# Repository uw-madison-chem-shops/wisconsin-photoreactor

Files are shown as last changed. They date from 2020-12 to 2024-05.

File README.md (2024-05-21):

# Wisconsin Photoreactor Platform (WPP)

An open source photoreactor platform. 3D printed enclosure, commercially available components, and a little bit of custom circuitry.

WPP photo

The WPP has been published in Organic Letters.
Please read our article to learn more about the motivation behind the WPP and to see examples of photochemistry being driven using this reactor.

>[Versatile Open-Source Photoreactor Architecture for Photocatalysis Across the Visible Spectrum](https://doi.org/10.1021/acs.orglett.1c01910); Philip P. Lampkin, Blaise J. Thompson, and Samuel H. Gellman; Org. Lett. 2021, 23, 13, 5277–5281

## Repository

This is an open source hardware project licensed under the CERN Open Hardware License Version 2 - Permissive.
Please see the LICENSE file for the complete license.

This repository is being mirrored to several version control systems in an attempt to ensure maximum availability.

| name             | url                                                                             |
| ---------------- | ------------------------------------------------------------------------------- |
| blaise           | https://git.blaise.zone/uw-madison-chem-shops/wisconsin-photoreactor.git/about/ | 
| Codeburg         | https://codeberg.org/uw-madison-chem-shops/wisconsin-photoreactor               |
| GitHub (primary) | https://github.com/uw-madison-chem-shops/wisconsin-photoreactor                 |
| GitLab           | https://gitlab.com/uw-madison-chem-shops/wisconsin-photoreactor                 |

## Safety

The Wisconsin Photoreactor Platform is for use by trained chemists.

WPP apparatuses utilize high-intensity light emitting diodes (LED) that can cause eye damage if proper safety precautions are not observed. 
A light-blocking shield should be utilized whenever operating a WPP apparatus.
Care must be taken to ensure the light-blocking shield employed adequately blocks light emitted by a WPP photon source from directly reaching a user.
Use of light-filtering safety glasses alongside a light-blocking shield can provide additional protection.

## Fabrication and Operation Instructions

This repository contains detailed instructions for fabrication, operation and documentation of WPP devices.
Please see [wpp-fabrication-operation.pdf](./fabrication-and-operation-instructions/wpp-fabrication-operation.pdf)

A video guide covering part sourcing, 3D-printing, electronics manufacturing, assembly and use of Wisconsin photoreactors is available on [youtube](http://www.youtube.com/watch?v=fkLr17i4FgE)

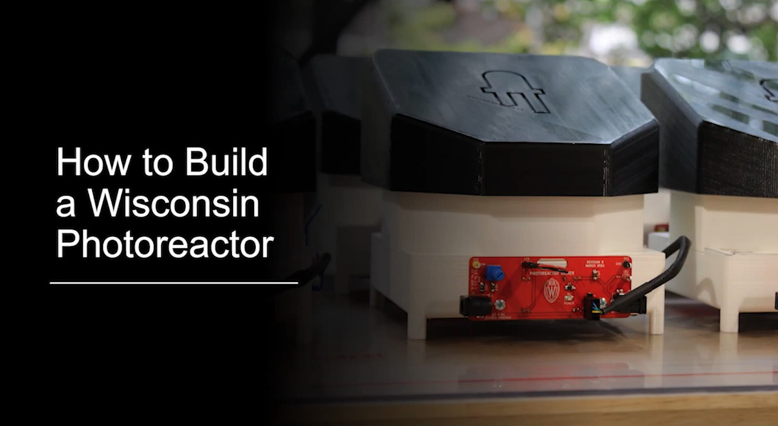
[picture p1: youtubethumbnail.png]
Wisconsin Photoreactor Platform Fabrication Video Guide (http://www.youtube.com/watch?v=fkLr17i4FgE)


## Enclosure

The WPP is designed around a mechanically robust and simple 3D printed enclosure.

Every WPP device has the same base, see directory `photoreactor-base`.
WPP reaction modules are meant to be switched based on the reaction vessel used.
See directory `photoreactor-reaction-modules` for our growing collection of reaction modules for common vessel types.
For safe WPP device operation, a light blocking shield is recommended. 
See directory `photoreactor-light-shield`, for a 3D-printable light-blocking cover for WPP devices.

## Electronics

The WPP incorporates small custom circuit boards providing control over reaction conditions.
Please see the fabrication instructions for more detailed information.

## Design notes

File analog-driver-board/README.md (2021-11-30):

# Analog Driver Board

A simple photoreactor driver board providing control over light intensity. This control is achieved through adjustment of the board-mounted potentiometer. No software is required, and multiple WPP reactors fitted with this board can be connected in series to a single power source. However, fan speed isn’t adjustable and is maintained at maximum.

Relative light intensity can be determined using the analog driver board test points and a multimeter. See operation instructions for more information.

The analog driver board is the recommended driver solution for a typical user.

## PCB

This PCB was designed using KiCAD version 5.
Refer to `driver.pdf` for schematic.
PCB images generated with [tracespace](https://github.com/tracespace/tracespace) follow.




## Bill of Materials

| reference      | value         | manufacturer | part number       | price | vendors |
| :------------- | :------------ | :----------- | :---------------- | :---- | :------ |
| C2             | 10u           | Yageo        | CC1206KKX7R8BB106 | $0.25 | [DigiKey](https://www.digikey.com/en/products/detail/yageo/CC1206KKX7R8BB106/5195365?s=N4IgTCBcDaIMJwIxgAwDYDSGAaB2ASgBwBCxi6IAugL5A) [Mouser](https://www.mouser.com/ProductDetail/Yageo/CC1206KKX7R8BB106/?qs=%2Fha2pyFadujG%252BB25mNGWlTAfaj3wXYmzjlPMfFLRNq4azOfH13S4tw%3D%3D) |
| D1             | (red)         | Lite-On      | LTST-C230KRKT     | $0.25 | [DigiKey](https://www.digikey.com/en/products/detail/lite-on-inc/LTST-C230KRKT/386857?s=N4IgTCBcDaIDIBUDKCC0BhMBmADAaQCU8EQBdAXyA) [Mouser](https://www.mouser.com/ProductDetail/Lite-On/LTST-C230KRKT/?qs=%2Fha2pyFadujtt9TjjkxDnLsTSvKz5QHldTfy80PY7mPtEP7ka44l7w%3D%3D) |
| J3, J4         | Barrel Jack   | CUI          | PJ-002A           | $1.50 | [DigiKey](https://www.digikey.com/en/products/detail/cui-devices/PJ-002A/96962) [Mouser](https://www.mouser.com/ProductDetail/CUI-Devices/PJ-002A/?qs=WyjlAZoYn51CKfAix9Mngw%3D%3D) |
| J5             | fan connector | Sullins      | PREC040SAAN-RC    | $0.50 | [DigiKey](https://www.digikey.com/en/products/detail/sullins-connector-solutions/PREC040SAAN-RC/2774814) |
| J7             | LED connector | Molex        | 0901471102        | $0.75 | [DigiKey](https://www.digikey.com/en/products/detail/molex/0901471102/3303846) |
| R1             | 6.8k          | Yageo        | RC1206FR-076K8L   | $0.10 | [DigiKey](https://www.digikey.com/en/products/detail/yageo/RC1206FR-076K8L/729028) |
| R2             | 100           | Yageo        | RC1206FR-07100RL  | $0.10 | [DigiKey](https://www.digikey.com/en/products/detail/yageo/RC1206FR-07100RL/728491?s=N4IgTCBcDaIAQCUDCBGMAGAbAMQQWnQHYV10EAZEAXQF8g) |
| R5             | 1k            | Yageo        | RC1206FR-071KL    | $0.10 | [DigiKey](https://www.digikey.com/en/products/detail/yageo/RC1206FR-071KL/728387?s=N4IgTCBcDaIEoGECMYAMA2AYnAtKg7EgNIAyIAugL5A) |
| RV1            | 2.2k          | Bourns       | 3362P-1-202TLF    | $3.00 | [DigiKey](https://www.digikey.com/en/products/detail/bourns-inc/3362P-1-202TLF/1232538?s=N4IgTCBcDaIMxwGxgAoFoCMawAYwBUAZAMRAF0BfIA) [Newark](https://www.newark.com/bourns/3362p-1-202tlf/trimmer-potentiometer-2kohm-10/dp/33M2835) |
| TP1            | (yellow)      | Keystone     | 5014              | $0.50 | [DigiKey](https://www.digikey.com/en/products/detail/keystone-electronics/5014/255336) |
| TP2            | (red)         | Keystone     | 5010              | $0.50 | [DigiKey](https://www.digikey.com/en/products/detail/keystone-electronics/5010/255332) |
| TP3            | (black)       | Keystone     | 5011              | $0.50 | [DigiKey](https://www.digikey.com/en/products/detail/keystone-electronics/5011/255333) |        |
| U2             | LED driver    | Mean Well    | LDD-1000L (pin)  | $6.00 | [DigiKey](https://www.digikey.com/en/products/detail/mean-well-usa-inc/LDD-1000L/7704722) [Allied](https://www.alliedelec.com/product/mean-well/ldd-1000l/70345765/) [Mouser](https://www.mouser.com/ProductDetail/MEAN-WELL/LDD-1000L?qs=JK6Bpmia%2FmvDNI%252Ba1vDDrA%3D%3D) [Newark](https://www.newark.com/mean-well/ldd-1000l/dc-dc-converter-analog-pwm-30w/dp/14AJ2201) [LEDSupply](https://www.ledsupply.com/led-drivers/mean-well-ldd-l-series-cc-step-down-mode)|

All prices are extended estimates in USD.
In general, these are overestimates, so this should be an upper-estimate on cost.
Many of these components can be substituted, so take the above as suggestions.
Boards themselves can be printed for approximately $5 each.

## Changelog

### Unprinted

### Revision C

#### Changed
- Removed wisconsin crest logo

#### Revision B

#### Fixed
- Fixedsign of LED terminals on silkscreen
- Voltage divider adjusted: R1 to 6.8k R2 to 100 ohm
- Adjusted voltage divider silkscreen

### Revision A

#### Added
- Initial design

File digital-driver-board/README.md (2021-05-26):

# digital-driver

A photoreactor driver board designed to be controlled digitally over I2C. For fabrication instructions, please see the fabrication and operation guide.

The digital driver is recommended for users who are experienced with electronics and interested in automating WPP devices.

## PCB

This PCB was designed using KiCAD version 5.
Refer to `driver.pdf` for schematic.
PCB images generated with [tracespace](https://github.com/tracespace/tracespace) follow.




Bill of Materials

| reference      | value         | manufacturer | part number          | price | vendors |
| :------------- | :------------ | :----------- | :------------------- | :---- | :------ |
|                | dip socket    | Mill-Max     | 110-93-308-61-001000 | $1.00 | [DigiKey](https://www.digikey.com/en/products/detail/mill-max-manufacturing-corp/110-93-308-61-001000/7734612) |
| C2             | 10u           | Yageo        | CC1206KKX7R8BB106    | $0.25 | [DigiKey](https://www.digikey.com/en/products/detail/yageo/CC1206KKX7R8BB106/5195365?s=N4IgTCBcDaIMJwIxgAwDYDSGAaB2ASgBwBCxi6IAugL5A) [Mouser](https://www.mouser.com/ProductDetail/Yageo/CC1206KKX7R8BB106/?qs=%2Fha2pyFadujG%252BB25mNGWlTAfaj3wXYmzjlPMfFLRNq4azOfH13S4tw%3D%3D) |
| C3             | 22u           | Yageo        | CC1206MKX7R7BB226    | $0.75 | [DigiKey](https://www.digikey.com/en/products/detail/yageo/cc1206mkx7r7bb226/7071713) |
| D1             | (red)         | Lite-On      | LTST-C230KRKT        | $0.25 | [DigiKey](https://www.digikey.com/en/products/detail/lite-on-inc/LTST-C230KRKT/386857?s=N4IgTCBcDaIDIBUDKCC0BhMBmADAaQCU8EQBdAXyA) [Mouser](https://www.mouser.com/ProductDetail/Lite-On/LTST-C230KRKT/?qs=%2Fha2pyFadujtt9TjjkxDnLsTSvKz5QHldTfy80PY7mPtEP7ka44l7w%3D%3D) |
| D2             | (blue)        | Lite-On      | LTST-C150TBKT        | $0.50 | [DigiKey](https://www.digikey.com/en/products/detail/lite-on-inc/LTST-C150TBKT/388526?s=N4IgTCBcDaIDIBUDKCC0BhAjAVgAwICEBpBEAXQF8g) |
| J1, J2         | i2c connector | JST          | S4B-PH-K-S(LF)(SN)   | $0.50 | [DigiKey](https://www.digikey.com/en/products/detail/jst-sales-america-inc/S4B-PH-K-S-LF-SN/926628) [Newark](https://www.newark.com/jst-japan-solderless-terminals/s4b-ph-k-s-lf-sn/connector-header-2mm-4-position/dp/38K8074) |
| J3, J4         | power input   | CUI          | PJ-002A              | $1.50 | [DigiKey](https://www.digikey.com/en/products/detail/cui-devices/PJ-002A/96962) [Mouser](https://www.mouser.com/ProductDetail/CUI-Devices/PJ-002A/?qs=WyjlAZoYn51CKfAix9Mngw%3D%3D) |
| J5             | fan connector | Sullins      | PREC040SAAN-RC       | $0.50 | [DigiKey](https://www.digikey.com/en/products/detail/sullins-connector-solutions/PREC040SAAN-RC/2774814) |
| J7             | LED connector | Molex        | 0901471102           | $0.75 | [DigiKey](https://www.digikey.com/en/products/detail/molex/0901471102/3303846) |
| PS1            | regulator     | CUI          | VXO7805-500-M-TR     | $3.00 | [DigiKey](https://www.digikey.com/en/products/detail/cui-inc/VXO7805-500-M-TR/11569188) [Newark](https://www.newark.com/cui/vxo7805-500-m-tr/non-isolated-dc-switching-regulator/dp/13AJ1536) |
| R1, R4, R6, R7 | 4.7k          | Yageo        | RC1206DR-074K7L      | $0.10 | [DigiKey](https://www.digikey.com/en/products/detail/yageo/rc1206dr-074k7l/5919134) |
| R2, R5         | 470           | Yageo        | RC1206FR-07470RL     | $0.10 | [DigiKey](https://www.digikey.com/en/products/detail/yageo/RC1206FR-07470RL/728934) |
| R3             | 10k           | Yageo        | RC1206FR-0710KL      | $0.10 | [DigiKey](https://www.digikey.com/en/products/detail/yageo/RC1206FR-0710KL/728483)  |
| U1             | microcontrol. | Microchip    | ATTINY85-20PU        | $1.50 | [DigiKey](https://www.digikey.com/en/products/detail/microchip-technology/attiny85-20pu/735469) [Newark](https://www.newark.com/microchip/attiny85-20pu/microcontroller-mcu-8-bit-attiny/dp/68T3808) |
| U2             | LED driver    | Mean Well    | LDD-1000L            | $6.00 | [DigiKey](https://www.digikey.com/en/products/detail/mean-well-usa-inc/LDD-1000L/7704722) [Allied](https://www.alliedelec.com/product/mean-well/ldd-1000l/70345765/) [Mouser](https://www.mouser.com/ProductDetail/MEAN-WELL/LDD-1000L?qs=JK6Bpmia%2FmvDNI%252Ba1vDDrA%3D%3D) [Newark](https://www.newark.com/mean-well/ldd-1000l/dc-dc-converter-analog-pwm-30w/dp/14AJ2201) [LEDSupply](https://www.ledsupply.com/led-drivers/mean-well-ldd-l-series-cc-step-down-mode)|

## I2C Interface

`<byte FAN SPEED>` `<byte LED INTENSITY>`

## Firmware

Find in "firmware" folder.

Use Arduino IDE.

We programmed the ATtiny85 using the sparkfun Tiny AVR Programmer: [PGM-11801](https://www.sparkfun.com/products/11801).

## Changelog

### Unprinted

#### Changed
- removed wisconsin crest logo

### Revision B

#### Fixed
- silk screen polarity markings for LED
- backwards I2C connectors

### Revision A

#### Added
- initial design

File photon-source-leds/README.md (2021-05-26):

# Photon Source LEDS

The WPP photon source consists of 3 high-power, single-color LEDs mounted onto an industry-standard 20 mm LED star package. 

WPP-compatible LED stars emitting narrow wavelength ranges across the UV-Visible spectrum are available from multiple vendors. A few are detailed below.

WPP-compatible custom LED stars mounted with 3.5 mm surface mount LEDs of any wavelength can be fabricated using a reflow oven. Please see the fabrication and operation guide for more information.

## List of compatible commercial LED stars

| color          | max emission (nm) | max current (mA)  | manufacturer | manufacturer part number | LEDsupply LED star part number | LEDsupply price | LED Star vendors | LED vendors |
| :------------- | :----------- | :----------- | :----------- | :----------------------- | :----------------------------- | :-------------- | :--------------- | :------------ |
| UVA            | 365       | 1200       | Inolux       | IN-C39CTOU2 	     	   | N/A (mounted by user)	        | N/A                | N/A | [DigiKey](https://www.digikey.com/en/products/detail/inolux/IN-C39CTOU2/9681227) [Mouser](https://www.mouser.com/ProductDetail/Inolux/IN-C39CTOU2/?qs=qSfuJ%252Bfl%2Fd4759YPTEyoag%3D%3D) |
| Violet         | 395        | 1200       | Inolux       | IN-C39CTOU5		       | N/A (mounted by user)          | N/A                | N/A | [DigiKey](https://www.digikey.com/en/products/detail/inolux/IN-C39CTOU5/9681233) [Mouser](https://www.mouser.com/ProductDetail/Inolux/IN-C39CTOU5/?qs=qSfuJ%252Bfl%2Fd6BLbca08ZG2g%3D%3D) |
| Blue           | 450        | 1500       | Cree, Inc.   | XTEARY-00-0000-000000N09  | CREEXTE-ROY-3	                | $10.10         | [LEDSupply](https://www.ledsupply.com/leds/cree-xlamp-xt-e-royal-blue-leds) | [DigiKey](https://www.digikey.com/en/products/detail/cree-inc/XTEARY-00-0000-000000N09/3744336) [Mouser](https://www.mouser.com/ProductDetail/Cree-Inc/XTEARY-00-0000-000000N09?qs=ygRr%2Ftkhtevu4HqMzfGc3w%3D%3D) |
| Cyan           | 495        | 1000       | Luxeon       | LXML-PE01-0080	    	   | 07007-PE000-K	                | $12.60           | [LEDSupply](https://www.ledsupply.com/leds/luxeon-rebel-color-leds) | [DigiKey](https://www.digikey.com/en/products/detail/lumileds/LXML-PE01-0080/3961255) [Mouser](https://www.mouser.com/ProductDetail/Lumileds/LXML-PE01-0080/?qs=7Vwje68bFtO%2F0g2M%252BAMdYQ%3D%3D) |
| Green          | 530        | 1000       | Cree, Inc.   | XPEBGR-L1-0000-00D01      | CREEXPE2-GRN-3		            | $10.50           | [LEDSupply](https://www.ledsupply.com/leds/cree-xlamp-xp-e2-color-high-power-led-star) | [DigiKey](https://www.digikey.com/en/products/detail/cree-inc/XPEBGR-L1-0000-00D01/4177200) [Mouser](https://www.mouser.com/ProductDetail/Cree-Inc/XPEBGR-L1-0000-00D01/?qs=rHlcMk0NooK%2FtCgm9PQ0pQ%3D%3D) |
| Amber          | 595        | 1000       | Luxeon       | LXML-PL01-0060		       | 07007-PL000-F	                | $12.60           | [LEDSupply](https://www.ledsupply.com/leds/luxeon-rebel-color-leds) | [DigiKey](https://www.digikey.com/en/products/detail/lumileds/LXML-PL01-0050/3961256) [Mouser](https://www.mouser.com/ProductDetail/Lumileds/LXML-PL01-0060?qs=7Vwje68bFtP0H6dN9OA%2FuA%3D%3D) |
| Orange         | 620        | 1000       | Cree, Inc.   | XPEBRO-L1-0000-00901	   | CREEXPE2-RDO-3                 | $10.50           | [LEDSupply](https://www.ledsupply.com/leds/cree-xlamp-xp-e2-color-high-power-led-star) | [DigiKey](https://www.digikey.com/en/products/detail/cree-inc/XPEBRO-L1-0000-00901/4177164) [Mouser](https://www.mouser.com/ProductDetail/Cree-Inc/XPEBRO-L1-0000-00901?qs=rHlcMk0NooLQklUEc3IqMg%3D%3D) |
| Red            | 660        | 1000       | Cree, Inc.   | XPEPHR-L1-0000-00801	   | CREEXPE-DRD-3                  | $10.50           | [LEDSupply](https://www.ledsupply.com/leds/cree-xlamp-xpe-high-power-led-star) | [DigiKey](https://www.digikey.com/en/products/detail/cree-inc/XPEPHR-L1-0000-00801/4895013) [Mouser](https://www.mouser.com/ProductDetail/Cree-Inc/XPEPHR-L1-0000-00801/?qs=3izLlwrMQ7lAtbsWL38zog%3D%3D) |
| NIR            | 730        | 1000       | Cree, Inc.   | XPEFAR-L1-0000-00601	   | CREEXPE-FRD-3	                | $12.00           | [LEDSupply](https://www.ledsupply.com/leds/cree-xlamp-xpe-high-power-led-star) | [DigiKey](https://www.digikey.com/en/products/detail/cree-inc/XPEFAR-L1-0000-00601/5303643) [Mouser](https://www.mouser.com/ProductDetail/Cree-Inc/XPEFAR-L1-0000-00601?qs=k72kBymvut%252B0JKg4b6%252BzNg%3D%3D) |

All prices are in USD.
In general, prices are overestimates, thereby providing an upper estimate on cost.

## Commercial LED emission spectra

LED emission spectra below were measured using an Ocean Insight USB2000 Spectrometer loaned by the [Goldsmith Group](https://goldsmith.chem.wisc.edu).

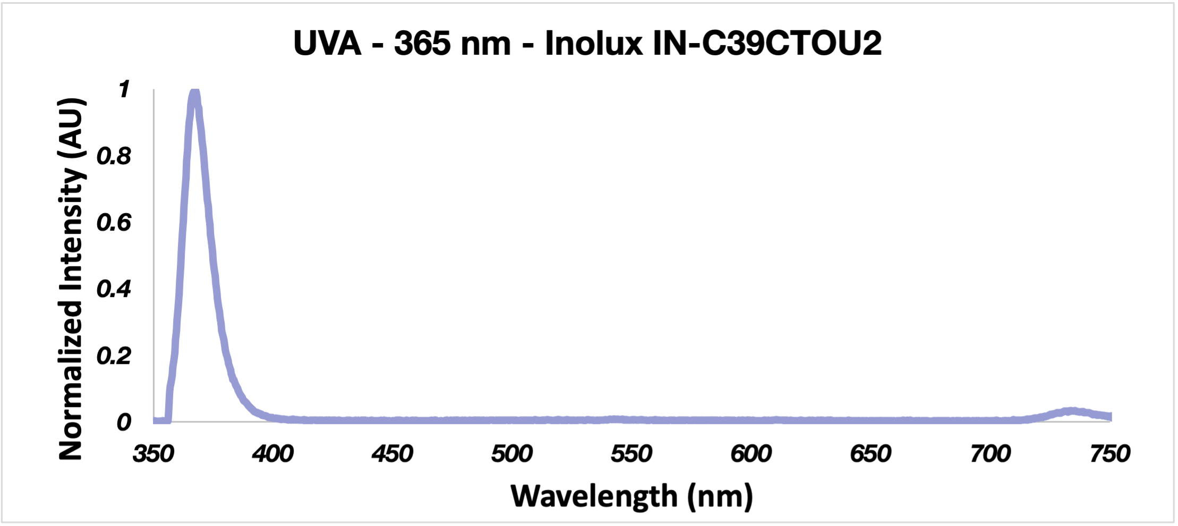
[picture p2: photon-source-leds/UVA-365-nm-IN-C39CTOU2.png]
UVA


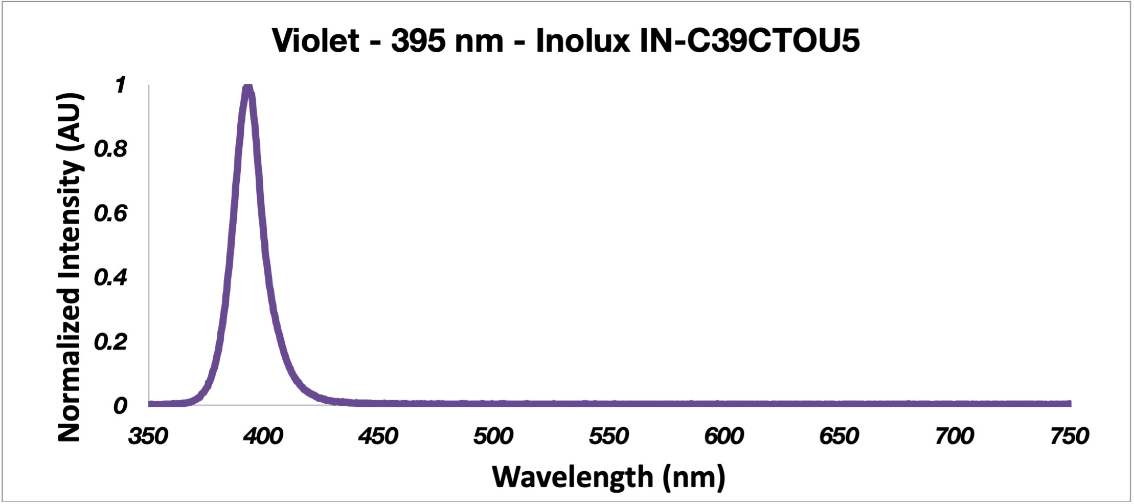
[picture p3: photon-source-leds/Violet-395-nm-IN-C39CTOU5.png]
Violet


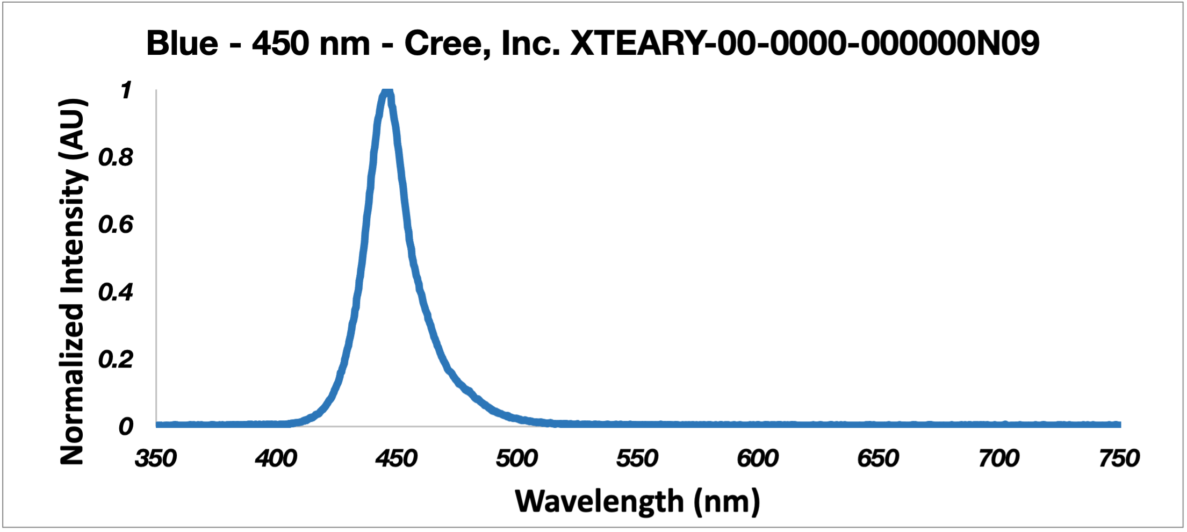
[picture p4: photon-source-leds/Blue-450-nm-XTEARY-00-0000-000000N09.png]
Blue


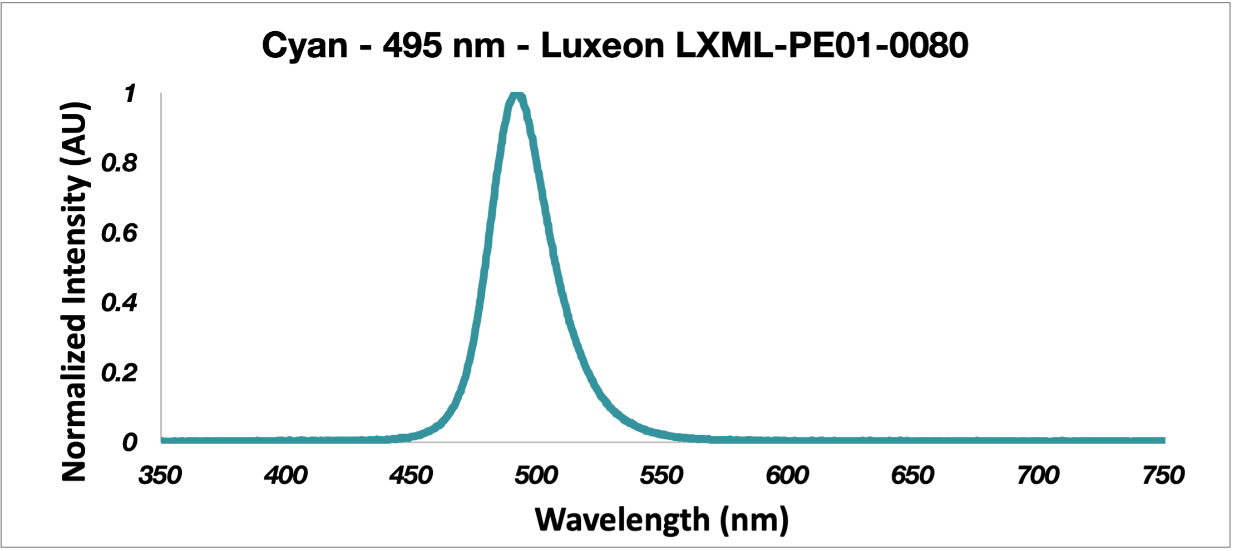
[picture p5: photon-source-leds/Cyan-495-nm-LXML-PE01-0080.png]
Cyan


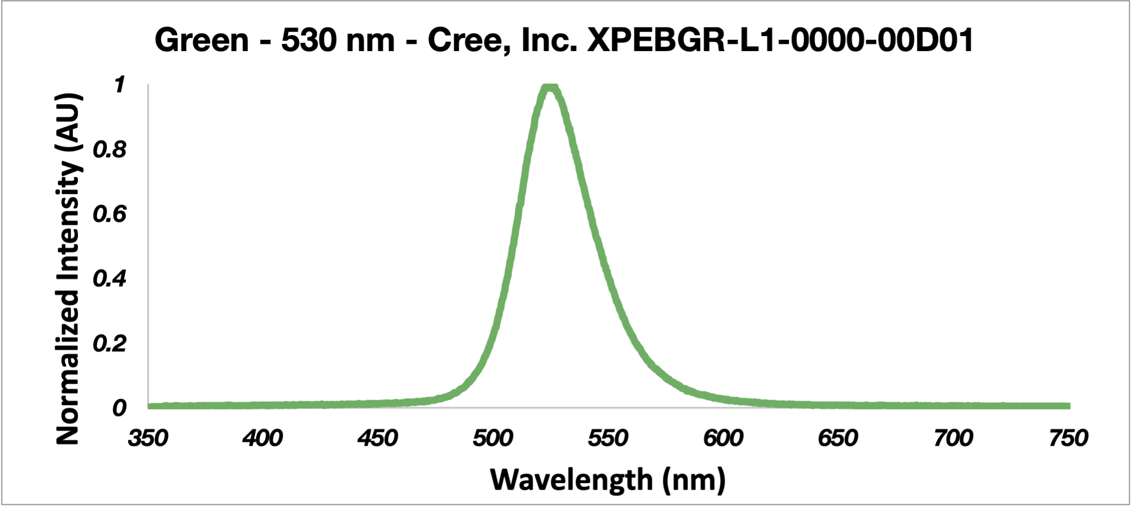
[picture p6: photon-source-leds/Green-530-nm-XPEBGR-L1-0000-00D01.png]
Green


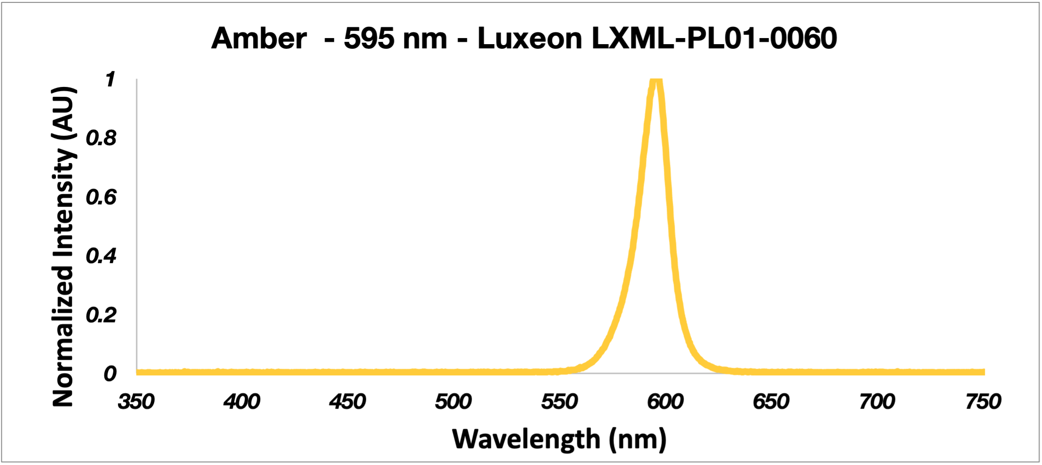
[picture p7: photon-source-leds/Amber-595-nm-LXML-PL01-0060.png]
Amber


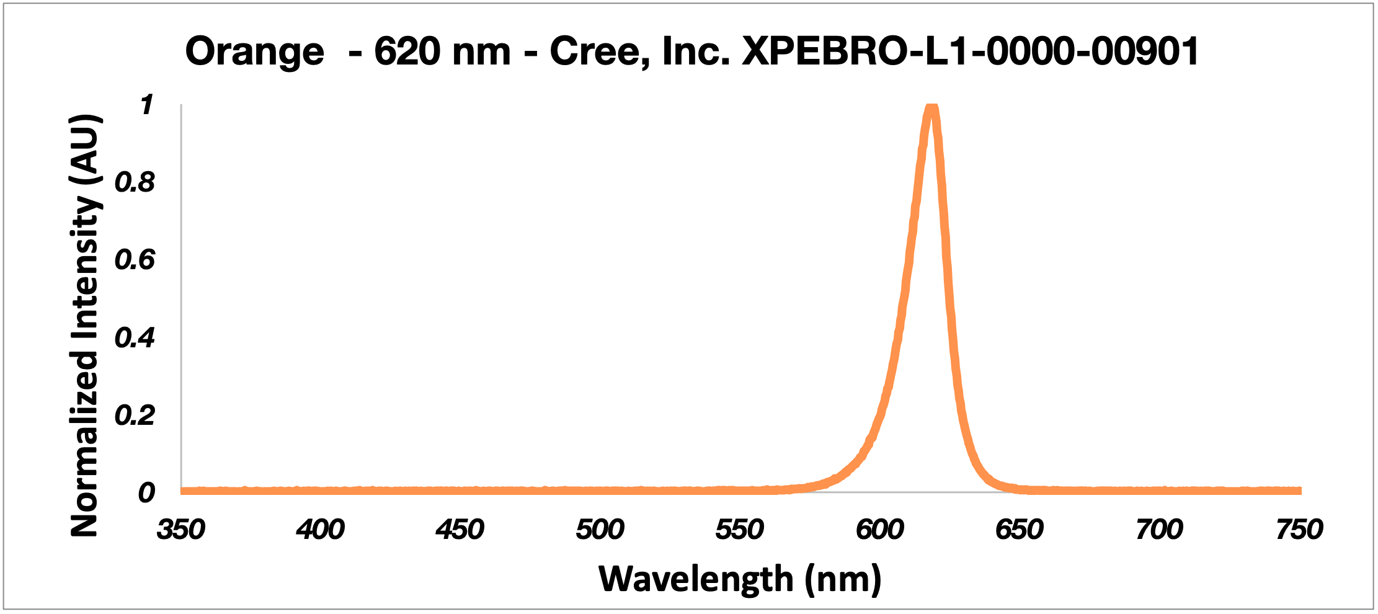
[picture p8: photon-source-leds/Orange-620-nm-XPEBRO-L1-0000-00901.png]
Orange


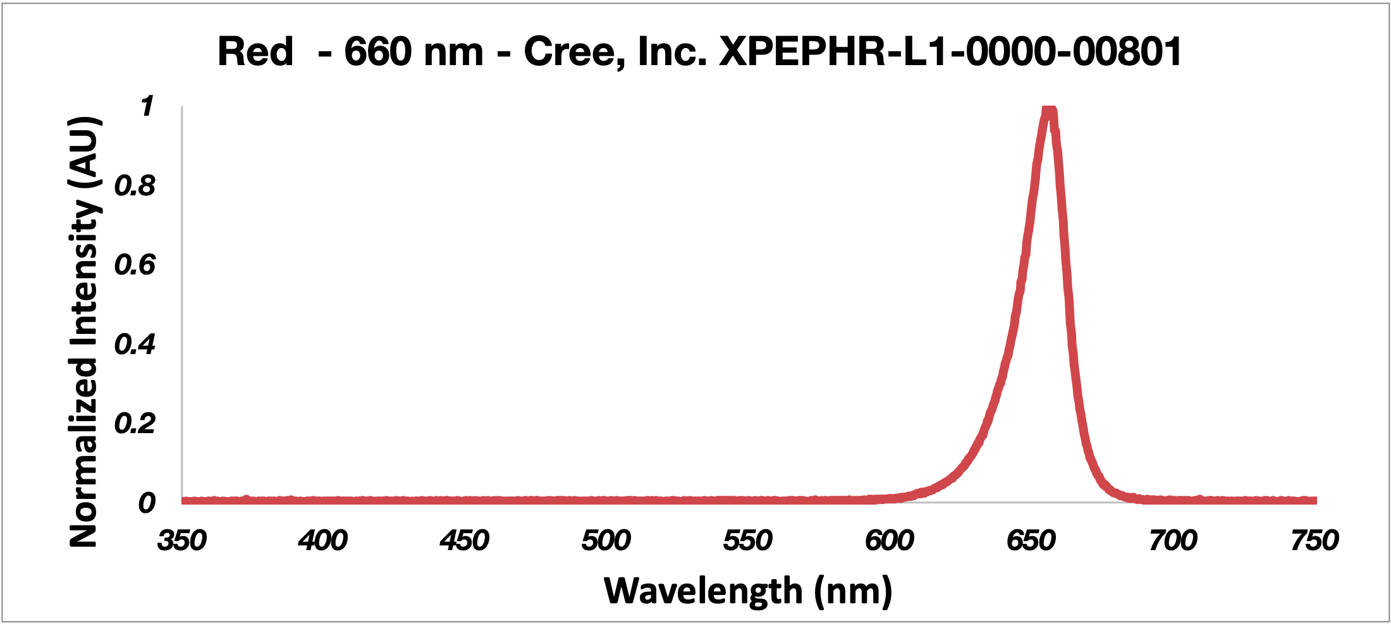
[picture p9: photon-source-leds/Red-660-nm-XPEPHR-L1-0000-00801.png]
Red


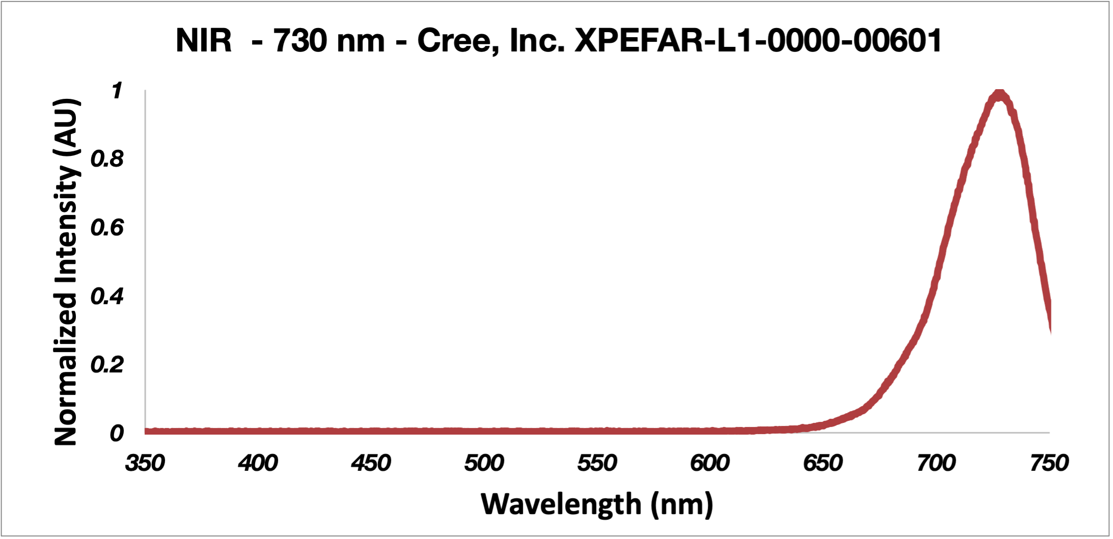
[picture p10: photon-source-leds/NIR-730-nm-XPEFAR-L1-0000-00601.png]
NIR


## Ordering Blank LED stars

The WPP base is designed to fit an industry-standard, 20 mm [Indus Star A008 high power LED modules](https://leddynamics.com/indus-star-a007-a008).

To order blank Indus Star A008 LED stars for custom LED star creation, contact [LEDsupply](https://www.ledsupply.com/contact-us), [LEDdynamics](https://leddynamics.com/contact-us) or other vendors.

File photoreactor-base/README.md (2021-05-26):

# WPP Standardized Base

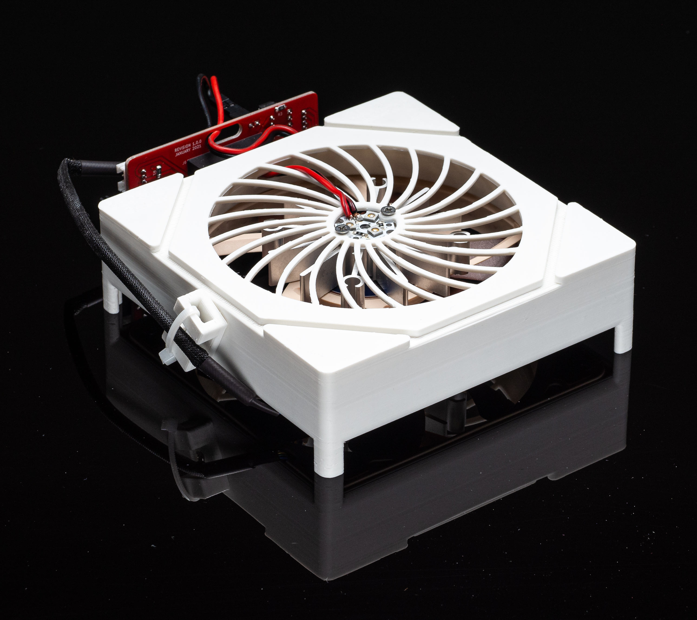
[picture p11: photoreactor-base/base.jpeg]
WPP base


The core structure of the Wisconsin Photoreactor Platform. Each reactor shares this component. It has a 130 mm by 130 mm footprint and is compatible with typical laboratory stir plates.

Through variation of the LED star integrated into a base, the user can control the wavelengths of light delivered by the photon source to a reaction vessel. 
Please see the fabrication and operation guide for LED star installation instructions. See `photon-source-leds` directory for list of LED stars confirmed compatible with the WPP architecture.

### Bill of Materials

| reference         | manufacturer | part number       | price  | vendors |
| :---------------- | :----------- | :---------------- | :----- | :------ |
| standoffs for PCB | RAF          | 4505-440-AL       | $1.00  | [DigiKey](https://www.digikey.com/en/products/detail/raf-electronic-hardware/4505-440-AL/7680509) [Newark](https://www.newark.com/raf-electronic-hardware/4505-440-al/no-plate-hex-male-female-standoffs/dp/95Y3120?st=4505-440-al) |
| LED star heatsink | Ohmite       | SV-LED-113E       | $3.00  | [DigiKey](https://www.digikey.com/en/products/detail/ohmite/SV-LED-113E/2509399) |
| LED star          | Various (see `photon-source-leds` directory) |
| heat-set inserts  | Virtjoule    |                   | $12.00  | [Amazon](https://www.amazon.com/gp/product/B07BH5X252/ref=ppx_yo_dt_b_asin_title_o09_s00?ie=UTF8&psc=1) |
| fan               | Noctua       | NF-A12x15 PWM     | $20.00 | [Amazon](https://www.amazon.com/Noctua-NF-A12x15-PWM-Premium-Quiet/dp/B071W6HJP6) |
| 1/4" screws       | Fastenal     | 0146455           |        |
| 3/4" screws       | Fastenal     | 72490             |        |

All prices are extended estimates in USD.
In general, these are overestimates, so this should be an upper estimate on cost.

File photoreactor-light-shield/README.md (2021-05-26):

# WPP light shield

WPP cover

A 3D-printable, light-blocking cover for Wisconsin Photoreactor Platform devices.
This generic cover module fits all WPP reaction modules. 
No customization of cover geometry is required.

The WPP light shield provides protection from direct exposure to light from WPP photon sources.
Printing the WPP light shield cover module using black filament is recommended to reduce light bounce.
Use of light-filtering safety glasses or additional light-blocking shields alongside the WPP light shield module is recommended for additional protection.

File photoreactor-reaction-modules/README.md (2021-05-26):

# Photoreactor Reaction Modules

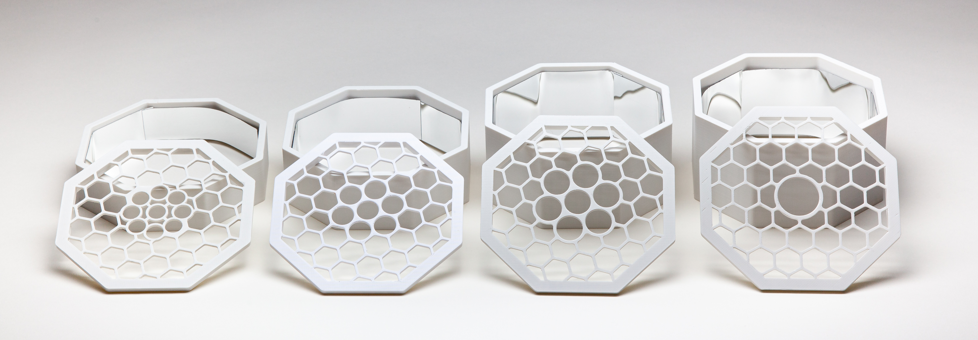
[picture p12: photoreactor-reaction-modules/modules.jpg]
WPP modules


A WPP reaction module consists of a reflective reaction chamber and rigid vessel holder. 

By modifying chamber height and adjusting holder geometry, one can produce modules compatible with reaction vessels of various types and sizes. 
Template reaction chamber and vessel holder CAD designs are provided in the `template` directory. 

CAD designs and 3D-printable models for modules compatible with various common reaction vessel are provided in this directory. A table listing vessels with already created reaction modules is offered below. 

## Reaction vessels with compatible modules

| vessel         | manufacturer       | manufacturer part number  |
| :------------- | :----------------- | :------------------------ |
| 2 mL Vial      | Fisher Scientific  | 03-338AA                  |
| 4 mL Vial      | Chemglass          | CG-4909-04                | 
| 8 mL Vial      | Chemglass          | CG-4909-03                |
| 10 mL Schlenk  | Synthware          | F580010	                  |
| 24 mL Vial     | VWR                | Vial: VWR 66012-044 Cap: Chemglass CG-4911-20 |

## Bill of Materials

The interior of WPP reaction chambers should be covered with reflective material. One option is offered below.

| reference         | manufacturer | part number       | price  | vendors |
| :---------------- | :----------- | :---------------- | :----- | :------ |
| mirror sheet      | Aneco        | 	B075R3MMX1       | $10.00 | [Amazon](https://www.amazon.com/gp/product/B075R3MMX1) |

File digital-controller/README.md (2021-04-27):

# Digital Controller

The digital driver board can be controlled using a "digital control unit."
Potential digital control units include Arduino or Rasberry Pi devices.
These control units can "supervise" the light intensity and fan speed of WPP devices fitted with digital driver boards.

Custom control unit firmware is required to interface with digital driver boards.
Open-source firmware for controlling a digital driver board with an Ardunio Uno is provided.
See the firmware files for use instructions.

Instructions on connecting an Arduino Uno to a digital driver board are provided in the fabrication and operation instructions.

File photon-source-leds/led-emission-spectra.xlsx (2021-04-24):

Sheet: Commercial LED Emission
Color | NIR |  | Red |  | Orange |  | Amber |  | Green |  | Cyan |  | Blue |  | Violet |  | UVA
Max Emission Wavelength | NIR - 730 nm |  | 660 nm |  | 620 nm |  | 595 nm |  | 530 nm |  | 495 nm |  | 450 nm |  | 390 nm |  | 365 nm
Manufacturer | Cree, Inc. |  | Cree, Inc. |  | Cree, Inc. |  | Luxeon |  | Cree, Inc. |  | Luxeon |  | Cree, Inc. |  | Inolux |  | Inolux
LED Manufactuerer Part Number | XPEFAR-L1-0000-00601 |  | XPEPHR-L1-0000-00801 |  | XPEBRO-L1-0000-00901 |  | LXML-PL01-0060 |  | XPEBGR-L1-0000-00D01 |  | LXML-PE01-0080 |  | XTEARY-00-0000-000000N09 |  | IN-C68QACTMU5 |  | IN-C68QACTMU2
LEDsupply 3-up LED Star Part Number | CREEXPE-FRD-3 |  | CREEXPE-DRD-3 |  | CREEXPE2-RDO-3 |  | 07007-PL000-F |  | CREEXPE2-GRN-3 |  | 07007-PE000-K |  | CREEXTE-ROY-3 |  | N/A |  | N/A
Wavelength | Intensity | Normalized Intensity | Intensity | Normalized Intensity | Intensity | Normalized Intensity | Intensity | Normalized Intensity | Intensity | Normalized Intensity | Intensity | Normalized Intensity | Intensity | Normalized Intensity | Intensity | Normalized Intensity | Intensity | Normalized Intensity
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

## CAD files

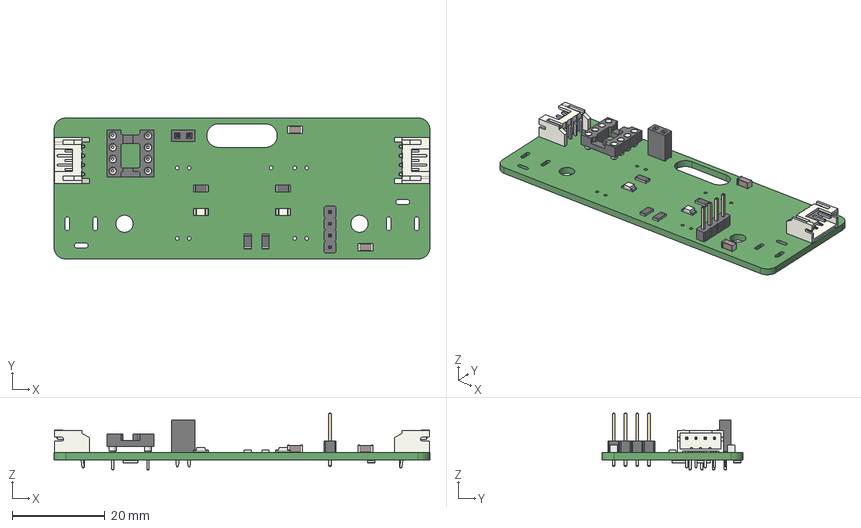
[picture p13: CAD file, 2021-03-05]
digital-driver-board/kicad/driver.step
81.3 x 30.5 x 12.3 mm

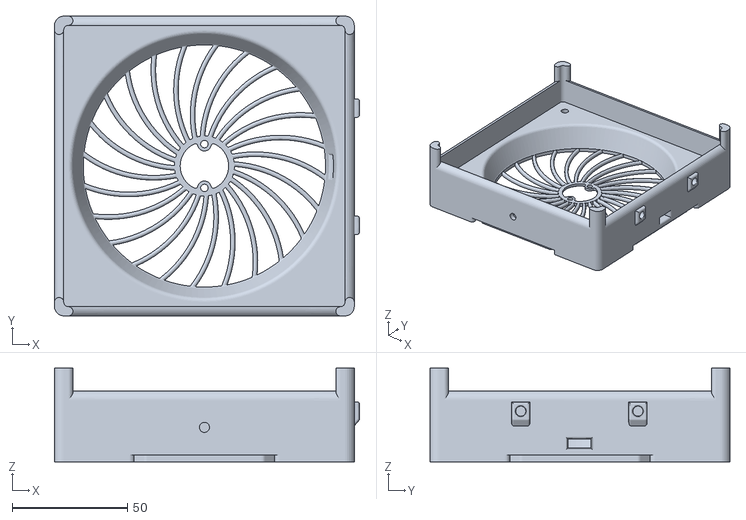
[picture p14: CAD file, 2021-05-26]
photoreactor-base/photoreactor_base.stl
132.2 x 130.0 x 40.7

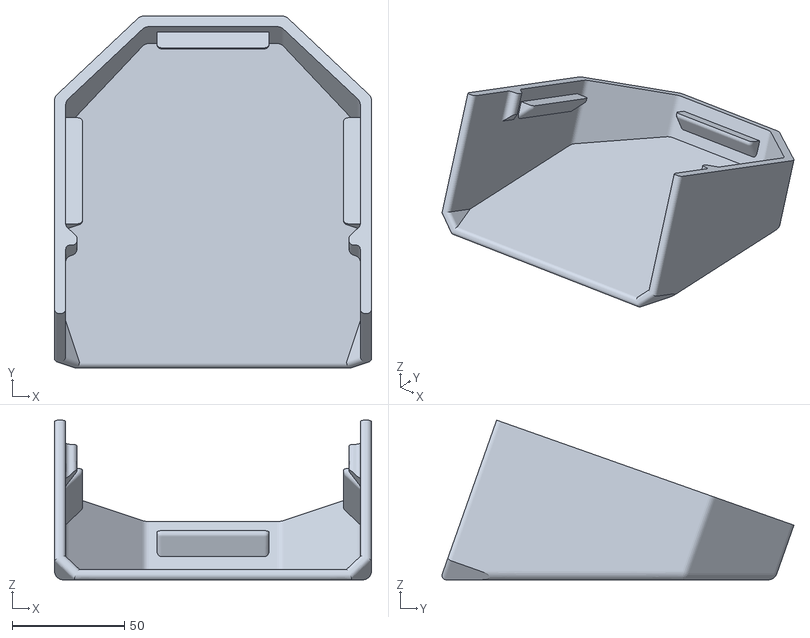
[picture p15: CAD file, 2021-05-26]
photoreactor-light-shield/light_shield.stl
141.0 x 156.5 x 71.0

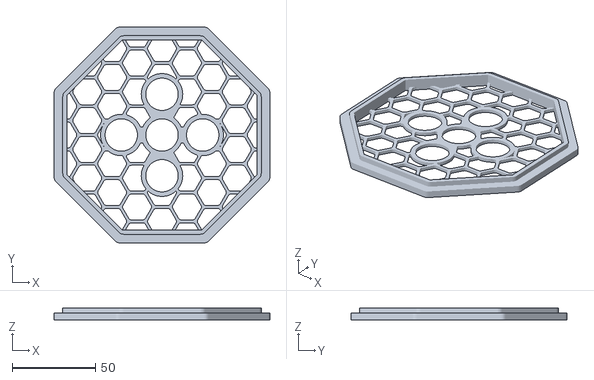
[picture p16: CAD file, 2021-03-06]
photoreactor-reaction-modules/10mL-Schlenk-Synthware-F580010/10ml-Schlenk-F580010-holder.stl
130.0 x 130.0 x 7.00

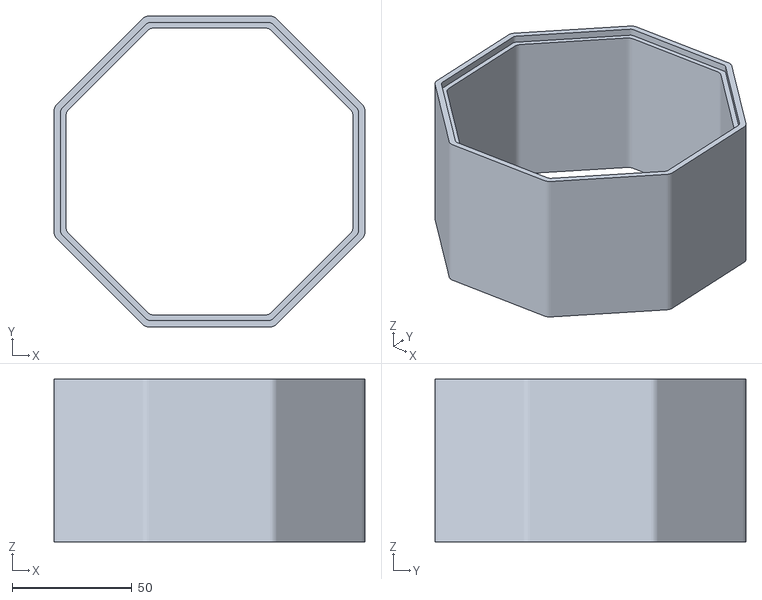
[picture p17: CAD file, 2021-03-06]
photoreactor-reaction-modules/24ml-vial-VWR-66012-044/24ml-vial-66012-044-chamber.stl
130.0 x 130.0 x 68.0

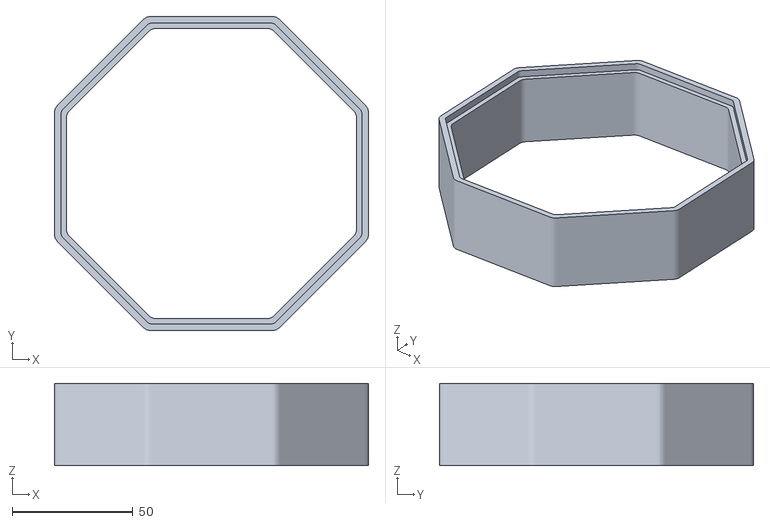
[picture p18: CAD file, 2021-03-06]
photoreactor-reaction-modules/2ml-vial-Fisher-Scientific-03-338AA/2mL-03-338AA-chamber.stl
130.0 x 130.0 x 34.0

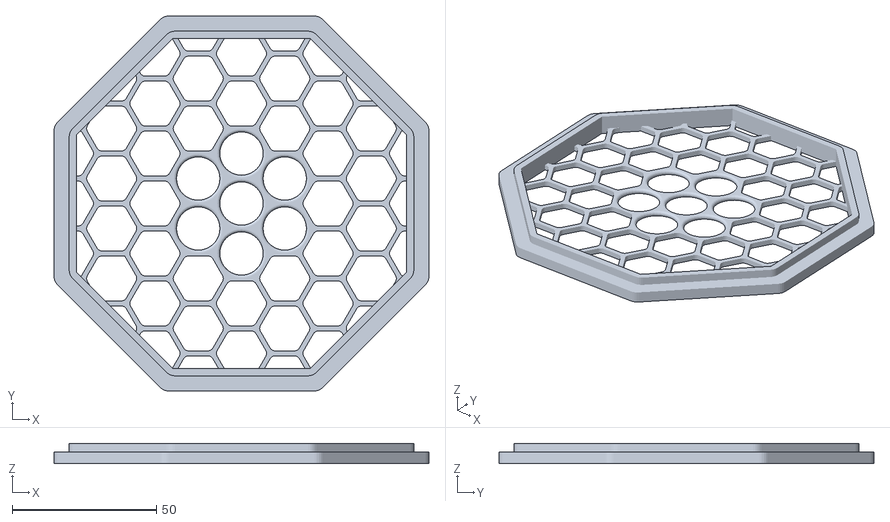
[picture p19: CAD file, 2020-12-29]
photoreactor-reaction-modules/4ml-vial-Chemglass-CG-4909-04/4ml-vial-CG-4909-04-holder.stl
130.0 x 130.0 x 7.00

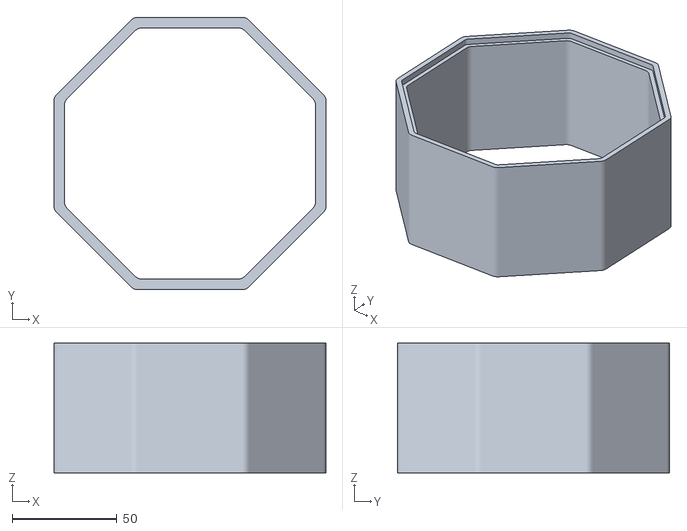
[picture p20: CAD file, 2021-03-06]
photoreactor-reaction-modules/8ml-vial-Chemglass-CG-4909-03/8ml-vial-CG-4909-03_chamber.stl
130.0 x 130.0 x 62.0

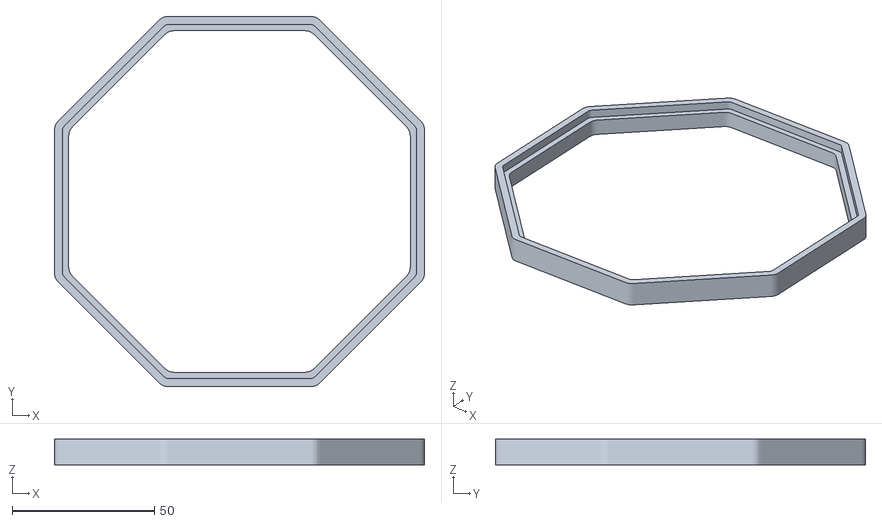
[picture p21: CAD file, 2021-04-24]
photoreactor-reaction-modules/template/template_chamber.stl
130.0 x 130.0 x 9.00

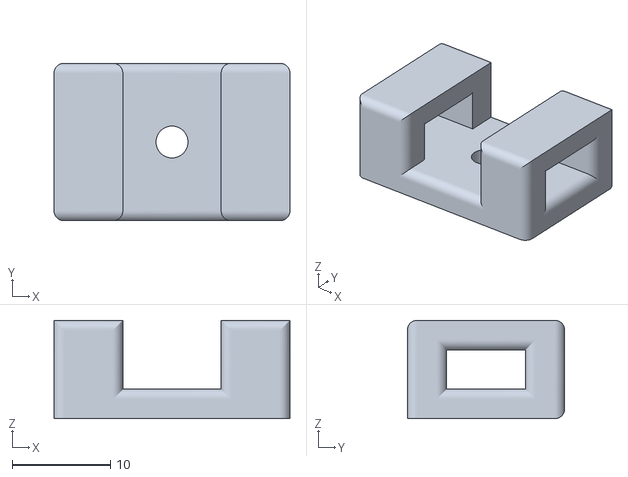
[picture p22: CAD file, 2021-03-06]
photoreactor-base/cable_anchor.stl
24.0 x 16.0 x 10.0

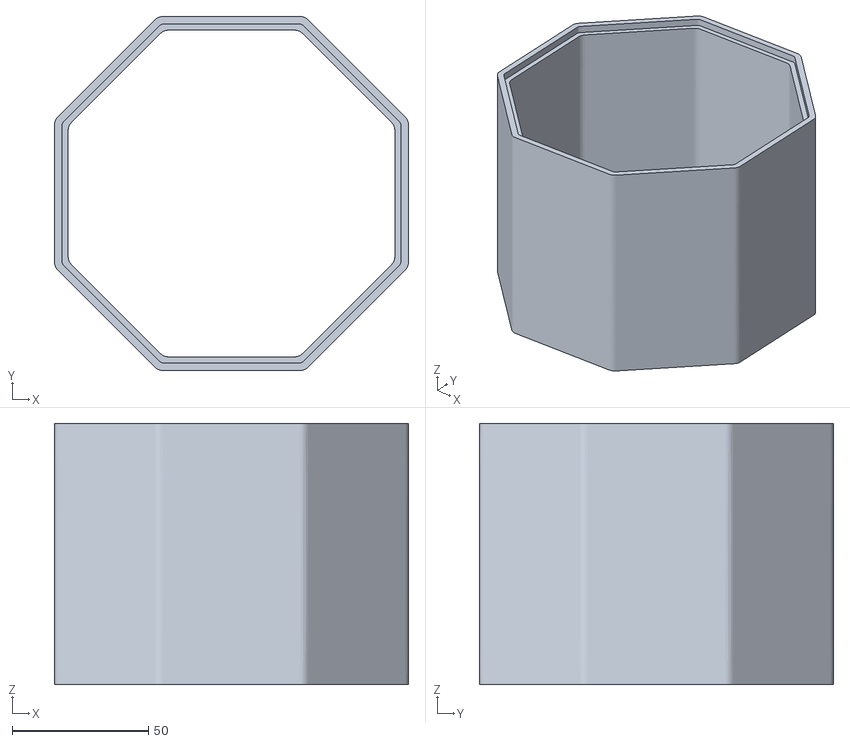
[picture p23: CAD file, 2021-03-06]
photoreactor-reaction-modules/10mL-Schlenk-Synthware-F580010/10ml-Schlenk-F580010-chamber.stl
130.0 x 130.0 x 96.0

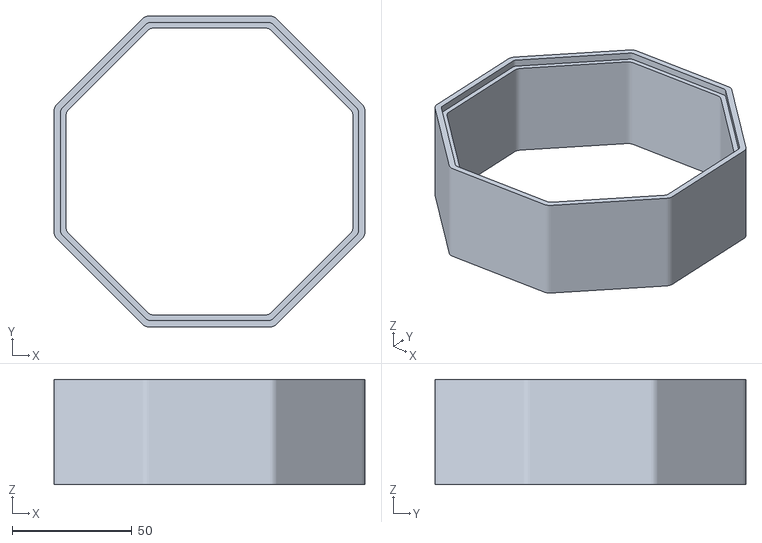
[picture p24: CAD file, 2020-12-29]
photoreactor-reaction-modules/4ml-vial-Chemglass-CG-4909-04/4ml-vial-CG-4909-04-chamber.stl
130.0 x 130.0 x 44.0

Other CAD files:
photoreactor-reaction-modules/24ml-vial-VWR-66012-044/24ml-vial-66012-044-holder.stl
photoreactor-reaction-modules/2ml-vial-Fisher-Scientific-03-338AA/2mL-03-338AA-holder.stl
photoreactor-reaction-modules/8ml-vial-Chemglass-CG-4909-03/8ml-vial-CG-4909-03_holder.stl
photoreactor-reaction-modules/template/template-holder.stl
photoreactor-base/cable_anchor.f3d
photoreactor-light-shield/light_shield.f3d
photoreactor-reaction-modules/10mL-Schlenk-Synthware-F580010/10ml-Schlenk-F580010-chamber.f3d
photoreactor-reaction-modules/24ml-vial-VWR-66012-044/24ml-vial-66012-044-chamber.f3d
photoreactor-reaction-modules/2ml-vial-Fisher-Scientific-03-338AA/2mL-03-338AA-chamber.f3d
photoreactor-reaction-modules/2ml-vial-Fisher-Scientific-03-338AA/2mL-03-338AA-holder.f3d
photoreactor-reaction-modules/4ml-vial-Chemglass-CG-4909-04/4ml-vial-CG-4909-04-chamber.f3d
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

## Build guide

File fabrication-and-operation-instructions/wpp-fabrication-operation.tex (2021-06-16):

%% document
\documentclass[11pt]{article}
\usepackage[letterpaper, portrait, margin=0.75in]{geometry}
\usepackage{setspace}
\usepackage{color}

% text
\usepackage[utf8]{inputenc}
\setlength\parindent{0pt}
\setlength{\parskip}{1em}
\renewcommand{\familydefault}{\sfdefault}
\newcommand{\RomanNumeral}[1]{\textrm{\uppercase\expandafter{\romannumeral #1\relax}}}

% math
\usepackage{amssymb}
\usepackage{amsmath}
\usepackage[cm]{sfmath}
\usepackage{commath}
\usepackage{multirow}
\DeclareMathAlphabet{\mathpzc}{OT1}{pzc}{m}{it}

% graphics
\usepackage{graphics}
\usepackage{graphicx}
\usepackage{epsfig}
\usepackage{epstopdf}
\usepackage{xpatch}
\usepackage{pdfpages}
\usepackage{float}

% each section begins new page
\let\stdsection\section
\renewcommand\section{\clearpage\stdsection}

% hyperref
\usepackage[colorlinks=true, linkcolor=black, urlcolor=blue, citecolor=black, anchorcolor=black]{hyperref}
\usepackage[all]{hypcap}  % helps hyperref work properly

\usepackage[shortlabels]{enumitem}
\setlist[enumerate, 1]{nosep}
\setlist[enumerate, 2]{nosep, topsep=-5ex}
\setlist[enumerate, 3]{nosep, topsep=-5ex}
\setlist[enumerate, 4]{nosep, topsep=-5ex}
\setlist[itemize, 1]{nosep}
\setlist[itemize, 2]{nosep, topsep=-5ex}
\setlist[itemize, 3]{nosep, topsep=-5ex}
\setlist[itemize, 4]{nosep, topsep=-5ex}

% bibliography
\usepackage[numbers]{natbib}

% title
\title{%
	\textbf{A Versatile Open-source Photoreactor Architecture\\ for Photocatalysis Across the Visible Spectrum}}

\author{\textbf{Philip P. Lampkin, Blaise J. Thompson and Samuel H. Gellman*} \\ \textit{University of Wisconsin-Madison, Madison, Wisconsin, 53706} \\ \\ \textit{Email: \href{mailto:gellman@chem.wisc.edu}{gellman@chem.wisc.edu}}}
\date{\today}

\begin{document}

\maketitle
\textbf{{\centering \huge Wisconsin Photoreactor Platform \\ Fabrication and Operation Guide \\}}

\vspace{10mm} %5mm vertical space
 


\tableofcontents

\section{Introduction}

Below are instructions for fabrication, operation and documentation of Wisconsin Photoreactor Platform (WPP) devices.

For access to all project files, documentation and resources, visit the Wisconsin Photoreactor Platform project repository on GitHub at \href{https://github.com/uw-madison-chem-shops/wisconsin-photoreactor}{https://github.com/uw-madison-chem-shops/wisconsin-photoreactor}.

\begin{figure}[H]
	
	\caption{(A) Unassembled WPP device comprised of a vessel holder, reaction chamber and standardized base fitted with a digital driver board. (B) Modular apparatus assembly.}
\end{figure}
A WPP device consists of a base, reaction module and reactor driver (Figure 1A).
The base houses the photon source and cooling fan.
The reaction module is comprised of a reflective reaction chamber and rigid vessel holder.
A digital driver board, analog driver board or simple circuit integrating a commercial light emitting diode (LED) driver can be fitted to the base to drive the reactor.

Each component is highly versatile, and apparatus assembly is fully modular (Figure 1B).
Through variation of each component, one can quickly produce bespoke WPP devices to meet specific research needs.

The WPP is a living project.
We encourage duplication, modification and expansion of our designs.
If you would like to contribute to the WPP project or notice a problem, please consider opening a pull request or issue on GitHub.

\section{Fabrication}

WPP devices are simple to fabricate.
To fabricate a WPP device, you'll need a soldering iron, electronics tweezers, thin nose pliers and a screwdriver at minimum.
The fabrication process is divided into three parts:

\begin{itemize}
	\item Base and photon source fabrication, described in \autoref{SEC:base}
	\item Reaction module fabrication, described in \autoref{SEC:enclosure}
	\item Reactor driver electronics fabrication, described in \autoref{SEC:electronics}
\end{itemize}

A WPP device is made up of many commercially available parts.
This guide assumes that you have already procured those parts.
The project repository provides README files containing a bill of materials for each component with part numbers and suggested vendors.

\subsection{Base and Photon Source} \label{SEC:base}

\begin{figure}[H]
	
	\caption{(A) Commercial 20 mm LED star mounted with 450 nm Cree, Inc. XT-E LEDs. (B) Top-down view of WPP base depicting integrated LED star.}
\end{figure}

The WPP architecture uses industry standard 20 mm ``LED star'' circuit boards mounted with 3 high-intensity LEDs to deliver photons to reaction vessels (Figure 2A).
LED stars are commercially available or can be easily fabricated.
The range of wavelengths provided by a LED star depends upon the emission profile of the mounted LEDs.
\textbf{\textit{Through variation of the LED star integrated into a WPP base (Figure 2B), the user can control the wavelengths of light delivered by the photon source to a reaction vessel.}}
An aluminum heatsink and cooling fan are integrated to keep the LED star from overheating.

A list of LED stars tested with the WPP platform is available in the 'photon-source-leds' subdirectory of the project repository.
It is easiest to use LED stars with pre-mounted LEDs.
Otherwise, you can fabricate custom LED stars with discrete LEDs and bare LED star circuit boards.
Custom LED star production requires a reflow oven.
All LEDs must have a maximum drive current of 1000 mA or higher.

\begin{figure}[H]
	
	\caption{(A) Unsoldered commercial LED star. (B) LED star with leads. (C) Connectors on other end of leads. (D) Connector sealed with heat-shrink tubing.}
\end{figure}

Fabrication of a WPP base begins with preparation of an LED star.
Solder leads onto your LED star, using the red positive and black negative convention (Figure 3A---B).
We recommend 22-gauge solid core wire.
This is often sold as "standard hookup" wire.
Soldering may be challenging, as the LED star itself will resist efforts to heat it.
Using lead-based solder with a low melting point may help.

Solder a connector to the end of the LED star.
Ensure the connection between the connector and wire is strong and has plenty of solder (Figure 3C).
Using heat-shrink tubing, seal the connection (Figure 3D).

\begin{figure}[H]
	
	\caption{(A) 3D-printed WPP base. (B) Securing a threaded inset into base.}
\end{figure}

Next, 3D-print a base enclosure and cable anchor.
Models for both are provided in the 'photoreactor-base' subdirectory of the project repository (Figure 4A).
The same base is shared by all WPP devices.

When interacting with the design files in our repository you will see several filetypes.
We have designed the WPP enclosure using Autodesk's Fusion 360 and included f3d design files for those who wish to extend or modify our designs.
Interacting with f3d files requires a Fusion 360 license, which is free for students and educators.
You will also find stl files in the repository.
These are common 3D-model exchange files that can be viewed with 3D modeling programs or printed with 3D-printers.

We recommend white PLA as the printing material. We have also used white ABS.
If you are printing yourself, follow the instructions provided by the manufacturer of your 3D-printer.
You will need to enable support material in your 3D slicer when printing the base enclosure.
We have successfully printed using the following printers:

\begin{itemize}
	\item Creality Ender 3
	\item Stratasys uPrint SE Plus
	\item Ultimaker 3 Extended
\end{itemize}

Any company or shop offering 3D printing as a service should accept our stl files without modification.
Once your base and cable anchor are printed, you may need to remove excess material with a razor blade or exacto-knife.

Each base contains seven threaded inserts.
These allow components such as an analog driver board and fan to rigidly attach to the base with screws.
Use a soldering iron to carefully heat the threaded inserts while pushing them into their cavities to set them (Figure 4B).

\begin{figure}[H]
	
	\caption{(A) Tapping aluminum heatsink. (B) LED star and heatsink installed into WPP base.}
\end{figure}

Now tap an aluminum heatsink for imperial 4-40 machine screws.
We used thread-forming tap: OSG 1400105300 with a pneumatic ``air-tapper'' (Figure 5).
The heatsink can be tapped by hand.
You only need to tap two of the innermost holes.

Install the LED star and heatsink into the WPP base using 1/4'' screws.
Ensure the LED wires face towards the hole in the side of the printed base.

\begin{figure}[H]
	
	\caption{(A) Integrated Fan. (B) Installed cable anchor with captured fan cord. (C) Metal standoffs screwed into base.}
\end{figure}

Install the fan.
Pay special attention to the orientation of the fan, including the location of the cord (Figure 6A).
Use 3/4'' screws here.
Then, install the cable anchor using a 1/4'' screw.
Use a zip tie to capture the fan cord (Figure 6B).
Finally, screw in the threaded standoffs (Figure 6C).
Your WPP base is now ready for use.

\begin{figure}[H]
	
	\caption{A WPP base fitted with an analog driver board with and without power.}
\end{figure}

To test the photoreactor base, simply screw a driver board to the threaded standoffs and plug the LED and fan into the board.
Pay special attention to the orientation of both connectors.
Your base should light up upon connection to power (Figure 7).
Remember to use proper eye protection.

\clearpage

\subsection{Reaction Module} \label{SEC:enclosure}

\begin{figure}[H]
	
	\caption{(A) Provided reaction modules for 2-, 4-, 8- and 24-mL vials. (B) WPP devices fitted with the provided reaction modules. (C) Single and (D) multiple reaction configurations for provide 4-mL module.}
\end{figure}

A WPP reaction module consists of a reaction chamber and vessel holder.
By modifying chamber height and adjusting holder geometry, one can produce modules compatible with reaction vessels of various types and sizes.
Fusion360 designs and stl models for modules compatible with 2-, 4-, 8- and 24-mL vials are provided in the 'photoreactor-reaction-modules' subdirectory of the project repository (Figure 8A—B).
Template reaction chamber and vessel holder Fusion360 designs are provided in the same directory.

We encourage you to design your own reaction modules if those provided in the project repository do not meet your needs.
If you do, we suggest you add your designs to the WPP repository so that others may benefit from your efforts.

A single reaction module can offer multiple layouts for reaction vessel placement.
For the provided modules, two vessel placement configurations exist.
First, the single reaction configuration, where one vessel is placed in the center of the module directly above the photon source (Figure 8C).
This configuration exposes one vessel to maximum light intensity.
Second, the multiple reaction configuration, where multiple vessels are placed in a circle around the photon source (Figure 8D).
This configuration exposes each vessel to less light relative to the single reaction configuration but provides equivalent exposure to each vessel.
\textbf{\textit{Through variation of the reaction module, the user can configure the reaction vessel type, size and placement within a WPP apparatus.}}

To fabricate a reaction module, simply 3D-print a reaction chamber and vial holder of your own design or taken from the 'reaction-modules' subdirectory of the project repository.

\begin{figure}[H]
	\centering
	
	\caption{(A) 4-mL reaction chamber. (B) Chamber lined with reflective material.}
\end{figure}

Once both parts are finished printing, cut reflective material to line the inside of the reaction chamber.
Remove the backing and stick the material to the chamber walls (Figure 9A---B).
It is fine to leave overlap around the interior.
The 3D printed vial holder requires no modification.
Your reaction module is now ready for use.

\clearpage

\subsection{Reactor Driver Electronics} \label{SEC:electronics}

\begin{figure}[H]
	\centering
	
	\caption{(A) Analog driver board. (B) Digital driver board. (C) Simple driver circuit.}
\end{figure}

A WPP device can be driven using an analog driver circuit board, a digital driver circuit board or a simple electronic circuit with a commercial LED driver (Figure 10).
All provide power to the cooling fan and current to the LEDs.
All utilize 1000 mA LED drivers. 
\textbf{\textit{Each provides different configurational capabilities.}}

Both driver boards are built around Mean Well's LDD-1000L LED driver module.
This module delivers current up to one amp.
The current delivered can be controlled electronically in several different ways.
Users wishing to understand this design should refer to Mean Well's datasheet.
Refer to the "analog-driver-board" and "digital-driver-board" directories in the online repository for design files for each board.

The analog driver board is designed to be exceedingly simple to fabricate and use.
The circuit accepts DC 12 V through a barrel jack.
A small knob is used to adjust light intensity.
Fan speed is not adjustable.
\textbf{We recommend that chemists interested in adopting the WPP architecture first build and test the analog driver board.}
Refer to \autoref{SEC:analog-driver} for analog driver board fabrication instructions and further explanation.

The digital driver board is made to be incorporated into an I$^2$C-based digital control system.
In addition to power, these boards have 4-pin connectors to carry the I$^2$C serial data.
\textbf{We recommend that chemists experienced in electronics and interested in automation of WPP devices or taking advantage of I$^2$C peripherals to expand device functionality use the digital driver board.}
Refer to \autoref{SEC:digital-driver} for digital driver board fabrication instructions and further explanation.

The simple driver circuit allows for any commercial 1000 mA LED driver to be used with a WPP device.
Refer to \autoref{SEC:simple-driver} for further explanation.

When interacting with the design files in our online repository you will see several different filetypes.
These circuit boards were designed using KiCad, a free and open source electronics CAD software.
All KiCad files are contained within the ``kicad'' subdirectories.
You may modify and extend these designs however you like.

Those wishing to produce the analog driver board or digital driver board designs should refer to the 'gerber' subdirectory.
Within this subdirectory you will find zip files containing everything necessary for production of printed circuit boards (PCB) of each board design.
You may upload these zip files to PCB manufacturers when ordering copies of our designs.

\clearpage
\subsubsection{Analog Driver Board} \label{SEC:analog-driver}

\begin{figure}[H]
	\centering
	
	\caption{(A) WPP devices fitted with analog driver boards connected in series. (B) Multimeter and WPP apparatus fitted with analog driver board. (C) Connection of multimeter to test points. (D) WPP apparatus at ~60 percent light intensity (1.5 V test point voltage)}
\end{figure}

\textbf{\textit{Through use of the analog driver board, one can reproducibly control WPP device light intensity via modulation of drive current.}}
This control is achieved through adjustment of the board-mounted potentiometer.
No firmware is required, and multiple WPP reactors can be connected in series to a single power source (Figure 11A).
However, fan speed isn’t adjustable and is maintained at maximum.
A full schematic of the analog circuit appears at the end of this section.
A bill of materials appears within the README file of the 'analog-driver-board' subdirectory of the project repository.

Relative light intensity can be determined using the analog driver board test points and a multimeter (Figure 11B-D).
The measured voltage can then be converted to relative light intensity using the values in Table 1.
These approximate values are derived from Mean Well's datasheet for the analog board’s LDD-1000L LED driver.
See the meanufacturer's datasheet for exact values.

\begin{table}[H]
	\centering
	\begin{tabular}{cc}
		\centering
		\textbf{Test Point Voltage} & \textbf{Approximate Relative Light Intensity} \\
		>2.45                       & 100\%                                          \\
		2.20                        & 90\%                                             \\
		2.95                        & 80\%                                             \\
		1.70                         & 70\%                                             \\
		1.45                        & 60\%                                              \\
		1.20                        & 50\%                                              \\
		10.95                        & 40\%                                            \\
		0.70                        & 30\%                                              \\
		0.45                        & 20\%                                              \\
		<0.45                        & 0\%
	\end{tabular}
	\caption{Test point voltage to approximate relative LED intensity conversion.}
	\label{tab:analog-board-conversion}
\end{table}

To fabricate an analog driver board, first order analog driver PCBs from a PCB manufacturer. Your PCB manufacturer will send you bare boards of the type seen in Figure 12A.

\begin{figure}[H]
	\centering
	
	\caption{(A) Blank analog driver board. (B) Analog driver board with labeled surface mount components.}
\end{figure}

Begin by soldering the surface mount components.
Refer to the analog driver schematic for part identities.
We recommend using thin solder, e.g. 0.015''.
The surface mount resistors and capacitors have no polarity.
The power indicator LED has a polarity---ensure that the small green line points towards ground (left).
Once finished, your analog board should look like that depicted in Figure 12B.

\begin{figure}[H]
	\centering
	
	\caption{(A) Analog driver board with potentiometer and connectors (B) Powered analog driver board.}
\end{figure}

Next, solder the connectors and potentiometer knob to the board (Figure 13A).
From now on we recommend standard gauge solder, e.g. 0.031''.
Then add the barrel jacks and test points.
With these added you may plug your board into power for the first time.
Either barrel jack can be plugged into power.
Your power indicator LED should illuminate (Figure 13B)

\begin{figure}[H]
	\centering
	
	\caption{Analog driver board fitted with Mean Well LDD-1000L LED driver.}
\end{figure}

Finally, solder the Mean Well LDD-1000L LED driver to the board (Figure 14).
This component goes on the back of the analog driver board.
The analog driver board is now ready for use.

\includepdf[landscape=true]{"../analog-driver-board/driver.pdf"}

\subsubsection{Digital Driver Board} \label{SEC:digital-driver}

\begin{figure}[H]
  \centering
  
  \caption{(A) WPP devices fitted with digital driver boards connected in series. (B) Powered WPP devices connected in series.}
  \label{FIG:digital-driver-network}
\end{figure}

\textbf{\textit{Through use of the digital driver board, one can control WPP device light intensity and fan speed using pulse width modulation.}} This control is achieved by interfacing a control unit, like an Arduino Uno, to the digital driver board using custom firmware. Multiple WPP devices with digital driver boards can be connected to a single control unit and power supply (Figure 15). Open-source firmware for interfacing digital driver boards with an Arduino Uno control unit is provided in the project repository. Other peripherals can be connected to digital driver boards to expand functionality, but firmware must be produced to interface with them.

To fabricate a digital driver board, first order digital driver PCBs from a PCB manufacturer. You will be sent bare boards of the type seen in Figure 16A.

\begin{figure}[H]
	\centering
	
	\caption{(A) Blank digital driver board. (B) Front and (C) back of digital driver board with labeled surface mount components.}
\end{figure}

Begin by adding the surface mount components to the front and back of the digital driver board PCB.
Refer to the digital driver schematic for part identities.
We recommend using thin solder, e.g. 0.015''.
The surface mount resistors and capacitors have no polarity.
Both indicator LEDs have a polarity---ensure that the small green line on both points towards ground (left).
Once finished, your digital driver board should look like that in Figure 16B and C.

\begin{figure}[H]
	\centering
	
	\caption{(A) Digital driver board mounted with power regulator. (B) Digital driver board with connectors, microcontroller socket, JST connectors and barrel jacks.}
\end{figure}

Next, solder the power regulator to the board (Figure 17A).
Pay special attention to the orientation of the regulator.
From now on we recommend standard gauge solder, e.g. 0.031''.
Solder on the connectors, microcontroller socket, JST connectors and barrel jacks (figure 17B).

\begin{figure}[H]
	\centering
	
	\caption{Digital driver board fitted with Mean Well LDD-1000L LED driver.}
\end{figure}

Finally, solder a Mean Well LDD-1000L LED driver to the board (Figure 18).
This component goes on the back of the digital driver board.
Physical fabrication of the digital driver board is now complete.
However, a microcontroller programmed with the necessary firmware must be installed onto the board to make it functional.

Each digital driver board requires an ATtiny85 microcontroller to act as the ``brains'' of the board.
This microcontroller allows the digital driver board to serve as a peripheral in an I$^2$C network supervised by a central control unit.
I$^2$C is a standard protocol for communication between digital circuits.
To "communicate" with the control unit, the ATtiny85 microcontroller must be programmed with firmware.
Firmware for the ATtiny85 microcontroller is provided within the '/digital-driver-board/firmware' subdirectory of the project repository.
This firmware can be edited if needed or you can create your own. 

\begin{figure}[H]
	\centering
	
	\caption{An ATtiny85 microcontroller programmer purchased from SparkFun (item number PGM-11801).}
\end{figure}

\clearpage

We recommend using the Arduino IDE and a commercial programmer to program ATtiny85 microcontrollers (Figure 19).
Follow the instructions provided by the manufacturer of your programmer to program microcontrollers with the provided firmware.
Note that each digital driver board has an address that is defined at the top of the firmware file programmed onto each microcontroller.
You should change the address of each microcontroller to be unique within the ``network'' of all I$^2$C peripherals connected to a single control unit.
Multiple digital driver boards with unique addresses may be networked together onto one I$^2$C bus by simply daisy-chaining the boards together, as shown in \autoref{FIG:digital-driver-network}.
You should physically label each microcontroller you program with its address.

\begin{figure}[H]
	\centering
	
	\caption{Digital driver board with a ATtiny85 microcontroller installed.}
\end{figure}

Once you have a programmed ATtiny85 microcontroller, install it into the socket of the digital driver board as shown in Figure 21.
Ensure the notch in the microcontroller is facing the correct direction (up and to the left).
Your digital driver board is now ready for use with a control unit.

\begin{figure}[H]
	\centering
	
	\caption{Digital driver board connected to an Arduino Uno.}
\end{figure}

\clearpage

There are many strategies one can employ to control digital driver boards.
We have provided firmware appropriate for using an Arduino Uno to control digital driver boards over a USB cable from any computer.
Find the firmware within the '/digital-controller/arduino-uno-controller/firmware' subdirectory of the project repository.
Flash this firmware onto an Arduino and connect at least the SCL, SDA, and GND pins to an Arduino Uno as shown in Figure 21.
This example firmware allows you to control multiple reactors by sending serial-over-USB commands from your computer.
Read the description at the top of the firmware file for details.

Many I$^2$C-compatible peripherals offering diverse functionalities are commercially available.
While the physical connectors may be different, our digital circuit is compatible with the following systems.

\begin{itemize}
  \item \href{https://learn.adafruit.com/introducing-adafruit-stemma-qt}{Adafruit STEMMA}
  \item \href{https://www.sparkfun.com/qwiic}{Sparkfun Qwiic}
  \item \href{https://www.seeedstudio.com/category/Grove-c-1003.html}{Seeed Grove}
  \item \href{https://store.ncd.io/?fwp_product_type=i2c-mini-modules}{NCD I2C Mini Modules}
\end{itemize}

I$^2$C peripherals in these families can be connected to digital driver boards to expand functionality, but software must be produced to interface with them.

\clearpage

\includepdf[landscape=true]{"../digital-driver-board/driver.pdf"}

\subsubsection{Simple Driver Circuit} \label{SEC:simple-driver}

\begin{figure}[H]
	\centering
	
	\caption{(A) Unassembled pieces of the simple LED driver circuit integrating a LUXdrive 1000mA PowerPuck LED driver (Part number: 2008B-1000). (B) Assembled circuit. (C) Powered circuit.}
\end{figure}

The LED driver circuit shown in Figure 22 is the simplest way to drive a WPP apparatus.
Neither light intensity nor fan speed can be configured when using the simple LED driver circuit.
Both are maintained at maximum power.
However, no circuit board fabrication is required, and any commercial 1000 mA LED driver can be used.

\section{Operation}

Once a WPP apparatus is configured with the desired photon source, reaction module and reactor driver, it is ready to drive photoreactions.

\begin{figure}[H]
  \centering
  
  \caption{A WPP apparatus with a 450 nm photon source, 4 mL reactor module and digital driver board on a standard laboratory stir plate conducting 6 simultaneous photoreactions in the multiple reaction configuration.}
\end{figure}

To conduct a photoreaction using a WPP device, an assembled apparatus should be placed on a lab stir plate, to provide reaction mixture stirring, and reaction vessels should be inserted into the apparatus in the desired layout (Figure 23).
The 130 by 130 mm footprint of the WPP architecture is compatible with typical stir plates.
A standard 12 V power supply can then be plugged into the reactor driver to turn on the device and start irradiation.
A single 12V 2 A power supply is sufficient to drive 2 WPP devices simultaneously.
A switch can be installed between the WPP apparatus and power supply to provide power switching.
A light-blocking shield should be used with WPP devices to limit light exposure.

Reaction and photon source cooling is provided by the fan integrated into the base.
Additional cooling can be achieved through placement of fans above the WPP apparatus or by placing a WPP device on a stir plate within a refrigerator or cold room.

Once finished, the WPP apparatus can be switched off by simply unplugging it. The apparatus can be disassembled for storage.

\section{Documentation}

WPP devices are easy to document.
Suggested below are the aspects of a WPP device that one should document whenever a WPP device is used in an investigation. 
Documenting each of these aspects will allow for precise reproduction of the exact WPP device used within a study. 

\subsection{Base and Photon Source} \label{SEC:doc-photon-source}

Users should report the following for each based and photon source used:

\begin{itemize}
	\item Max emission wavelength for LEDs.
	\item Manufacturer and part number for LEDs.
	\item Supplier and part number for LED star (if commercial).
\end{itemize}

This information enables precise reproduction of WPP photon sources. Characterization of a photon source’s emission profile using a spectrometer is recommended but not required for reproduction. Emission profiles for commercial LEDs are supplied in part datasheets provided by manufacturers.

\subsection{Reaction Module} \label{SEC:doc-reaction modules}

Users should provide and report the following for each reaction module used:

\begin{itemize}
	\item Original CAD designs for both module parts.
	\item 3D-printable models for both module parts.
	\item Photos of each reaction vessel placement configuration.
	\item Manufacturer and part number for reaction vessel.
\end{itemize}

These provisions enable precise reproduction of reaction modules. Documenting the height a vessel is held above the photon source is recommended but not required for reaction module reproduction. All reaction modules provided in the project repository hold vessels a standardized 7 mm above the photon source.

\subsection{Reactor Driver Electronics} \label{SEC:doc-reactor-drivers}

As each reactor driver offers different configurational abilities, each requires different levels of documentation for exact reproduction.

\subsubsection{Analog Driver Board } \label{SEC:doc-analog-driver}

Users should report the following when an analog driver board is used:

\begin{itemize}
	\item Measured test point voltage.
	\item Relative intensity at which LEDs are driven (0 to 100\%).
\end{itemize}

These provisions enable precise reproduction of reaction conditions for transformations carried out using WPP devices fitted with analog driver boards.

\subsubsection{Digital Driver Board} \label{SEC:doc-digital-driver}

Users should provide and document the following when a digital driver board is used:

\begin{itemize}
	\item Firmware used to operate the digital driver board, control unit and any other peripherals.
	\item Relative intensity at which LEDs are driven (0 to 100\%).
	\item Relative fan speed (0 to 100\%).
\end{itemize}

These provisions enable precise reproduction of reaction conditions for transformations carried out using WPP devices fitted with digital driver boards.

\subsubsection{Simple Driver Circuit} \label{SEC:doc-simple-driver}

Users should report the following when a simple LED driver circuit is used:

\begin{itemize}
	\item Manufacturer and part number for LED driver.
\end{itemize}

This information enables reproduction WPP devices fitted with the simple LED driver circuit.

\section{Safety}

WPP reactors utilize high-intensity light emitting diodes (LED) that can cause eye damage if proper safety precautions are not observed.

A light-blocking shield should be utilized whenever operating a WPP apparatus. 
Care must be taken to ensure the light-blocking shield employed adequately blocks light emitted by a WPP photon source from directly reaching a user.

\begin{figure}[H]
	\centering
	
	\caption{WPP device fitted the provided light shield cover module printed in black PLA.}
\end{figure}

A 3D printable light-blocking cover module for WPP devices is provided in the 'photoreactor-light-shield' subdirectory of the project repository.
The WPP light shield prevents direct exposure of users to light emitted by WPP photon sources. 
We recommend printing the WPP light shield using black filament to minimize light bounce (Figure 24).

Use of light-filtering safety glasses alongside a light-blocking shield can provide additional protection from high-intensity light.

\section{Acknowledgments}

We thank Dr. Ilia A. Guzei and Sebastian Thompson of UW-Madison for photography and help fabricating custom LED stars, respectively. 

\end{document}

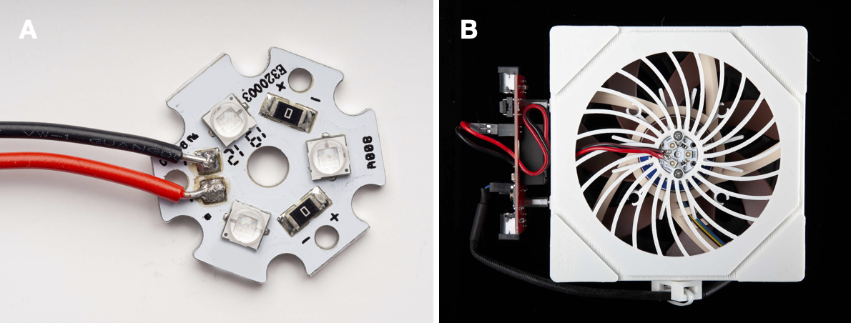
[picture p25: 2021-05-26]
fabrication-and-operation-instructions/fig2.png

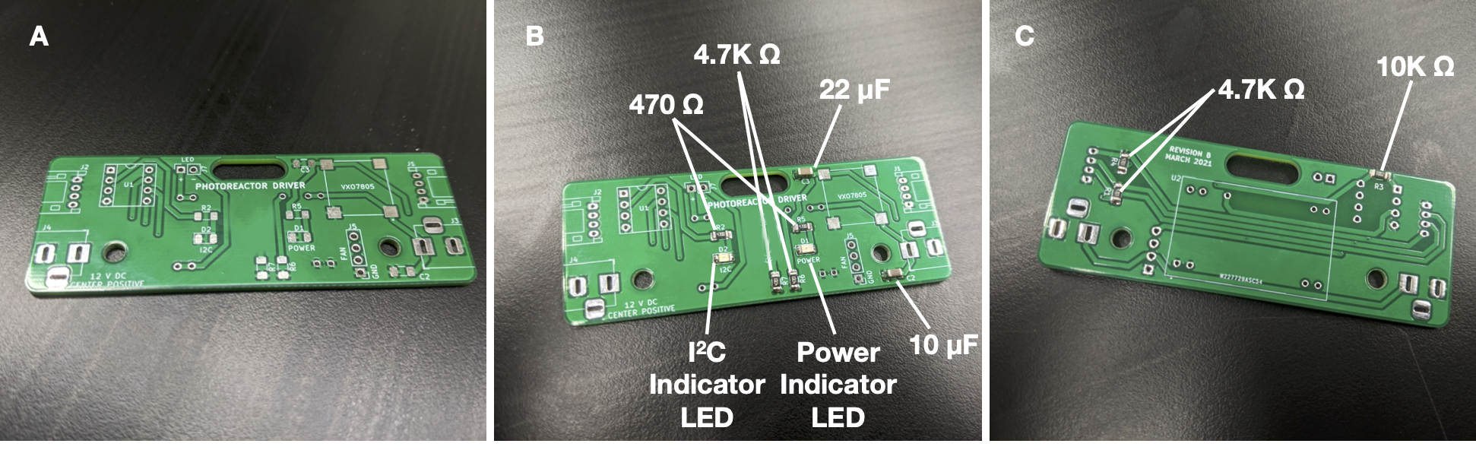
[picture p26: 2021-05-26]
fabrication-and-operation-instructions/fig16.png

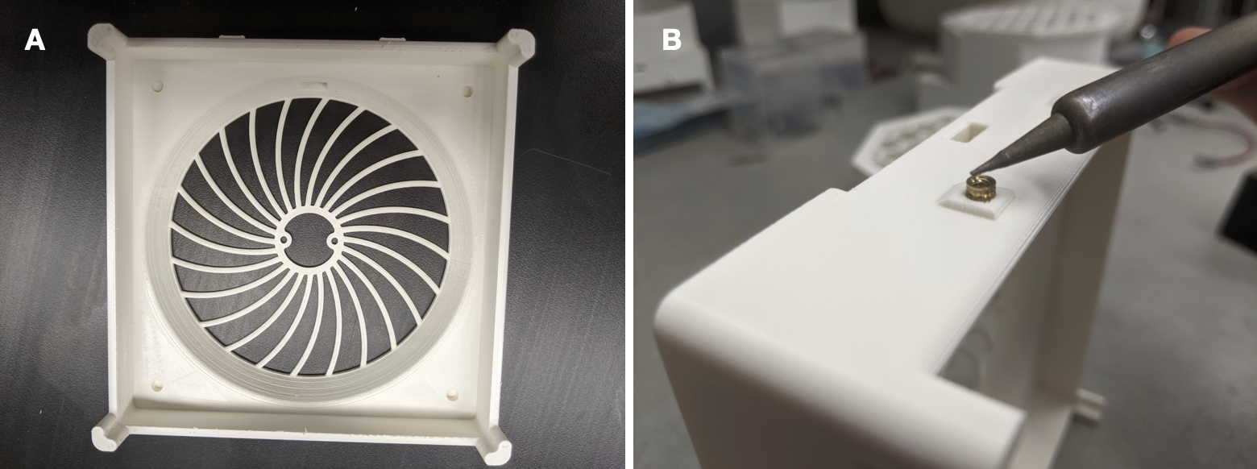
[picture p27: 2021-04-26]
fabrication-and-operation-instructions/fig4.png

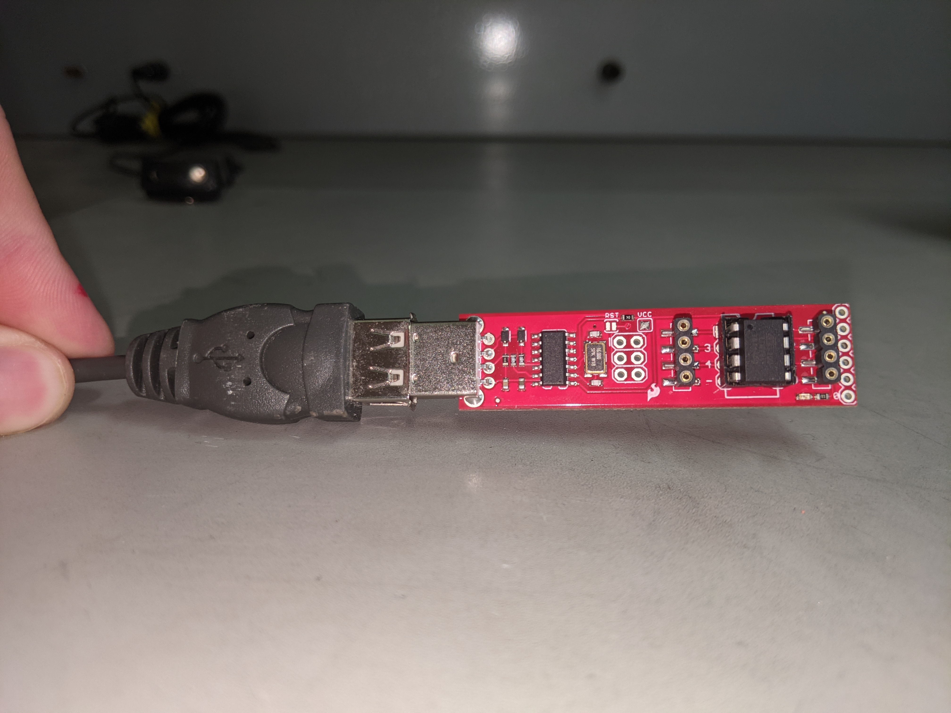
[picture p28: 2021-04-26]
fabrication-and-operation-instructions/tiny-programmer.jpg

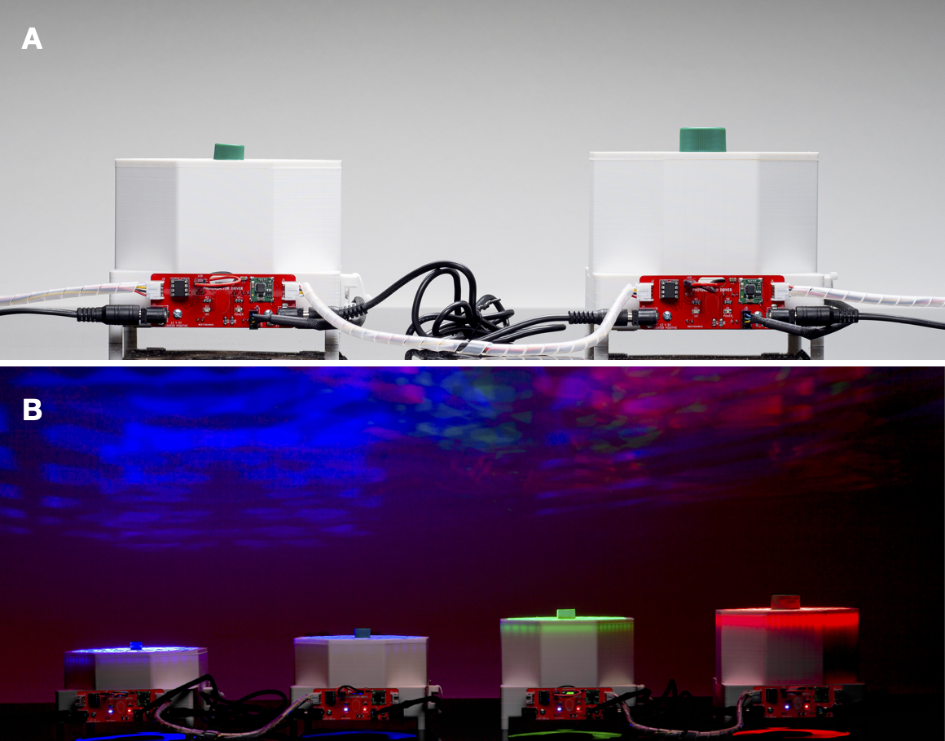
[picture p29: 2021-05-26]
fabrication-and-operation-instructions/fig15.png

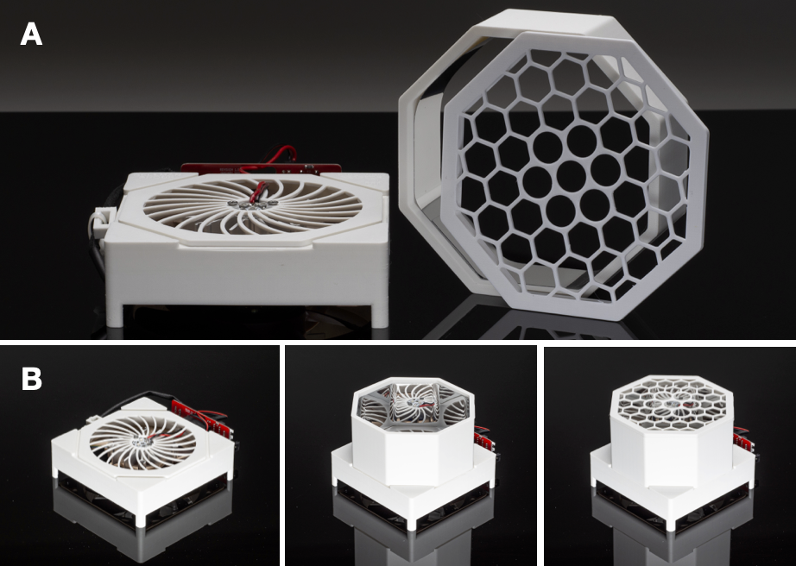
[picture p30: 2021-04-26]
fabrication-and-operation-instructions/fig1.png

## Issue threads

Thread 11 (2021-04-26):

### ISSUE TITLE
Standardize on LED to Driver board male connector

### ISSUE THREAD

**Issue by plampkin** [uw-madison-chem-shops/wisconsin-photoreactor#11]
and take a photo of it to put into fabrication guide!

**Comment by untzag** [comment]
I'm thinking our official recommendation should be to just solder to the same breakable male headers we use for the fan. Heatshrink preferred if available. That way we have zero extra parts in the BOM.

**Comment by plampkin** [comment]
That's perfect! I'll take a photo of that setup tomorrow.

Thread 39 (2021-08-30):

### ISSUE TITLE
Potential to improve manufacturability

### ISSUE THREAD

**Issue by severon10290** [uw-madison-chem-shops/wisconsin-photoreactor#39]
Currently, the top chamber and vile holder are separate parts. If these parts do not need to be removed individually, they could be combined into one piece printed upside down. This would reduce the part count and potentially reduce the time to print each separately. As each vile size appears to have its own height for the associated chamber, this could also make it easier to use by moving the potential for a chamber that is too small to be selected. 

Alternatively, if the top piece needs to be removable, it could be laser cut from a thicker, potentially clear, sheet. This would most likely reduce the fabrication time; however, it would add some complication to fabrication by adding another machine needed to create the device.

**Comment by untzag** [comment]
> Currently, the top chamber and vile holder are separate parts. If these parts do not need to be removed individually, they could be combined into one piece printed upside down.

Actually I agree. It's not clear to me why those two are separate parts. @plampkin would know.

**Comment by plampkin** [comment]
Excellent question! These parts are separated for 2 major reasons:

1. Easy/fast broken part replacement - The part of our design that receives the most wear and is the most prone to breaking is the vial holder. This is due to the the process of repeatedly inserting and removing vials gradually wearing down the plastic. To extend the life of the overall device, it's better to keep the vial holder separate from the reaction chamber (which receives essentially no wear under standard use). 

2. Compatibility of different reaction vessels - Should someone want to run a reaction in a RBF, or some other non-vial reaction vessel that can't easily be inserted into a combined chamber + vial holder unit, having separate parts simplifies the process of designing compatible parts. Though it might be overly optimistic of me to assume anyone would want to run reactions in anything beside vials.

**Comment by untzag** [comment]
OK, I think @plampkin speaks from experience here. Even though a single piece would be easier to 3D print there are clearly practical reasons to make two.

Furthermore @severon10290 your idea of laser cutting the top panels is great if we need to make 100, but I think at our current scale it's simplest to just keep it all on the 3D printer.

Closing this issue, feel free to reopen if more discussion is warranted.

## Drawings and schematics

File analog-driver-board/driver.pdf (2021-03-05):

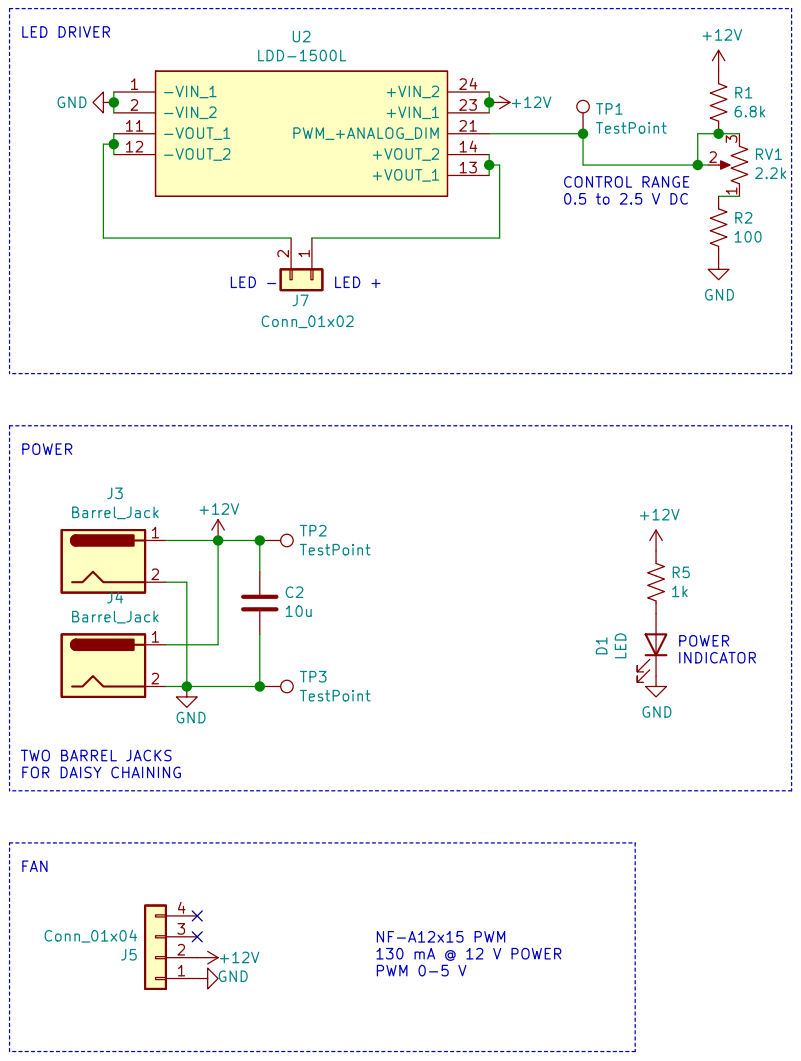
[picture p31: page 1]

blaise.thompson@wisc.edu
Blaise Thompson
Gellman Group
Department of Chemistry
Id: 1/1 Title: Analog Photoreactor Driver File: driver.sch Sheet: / University of Wisconsin-Madison

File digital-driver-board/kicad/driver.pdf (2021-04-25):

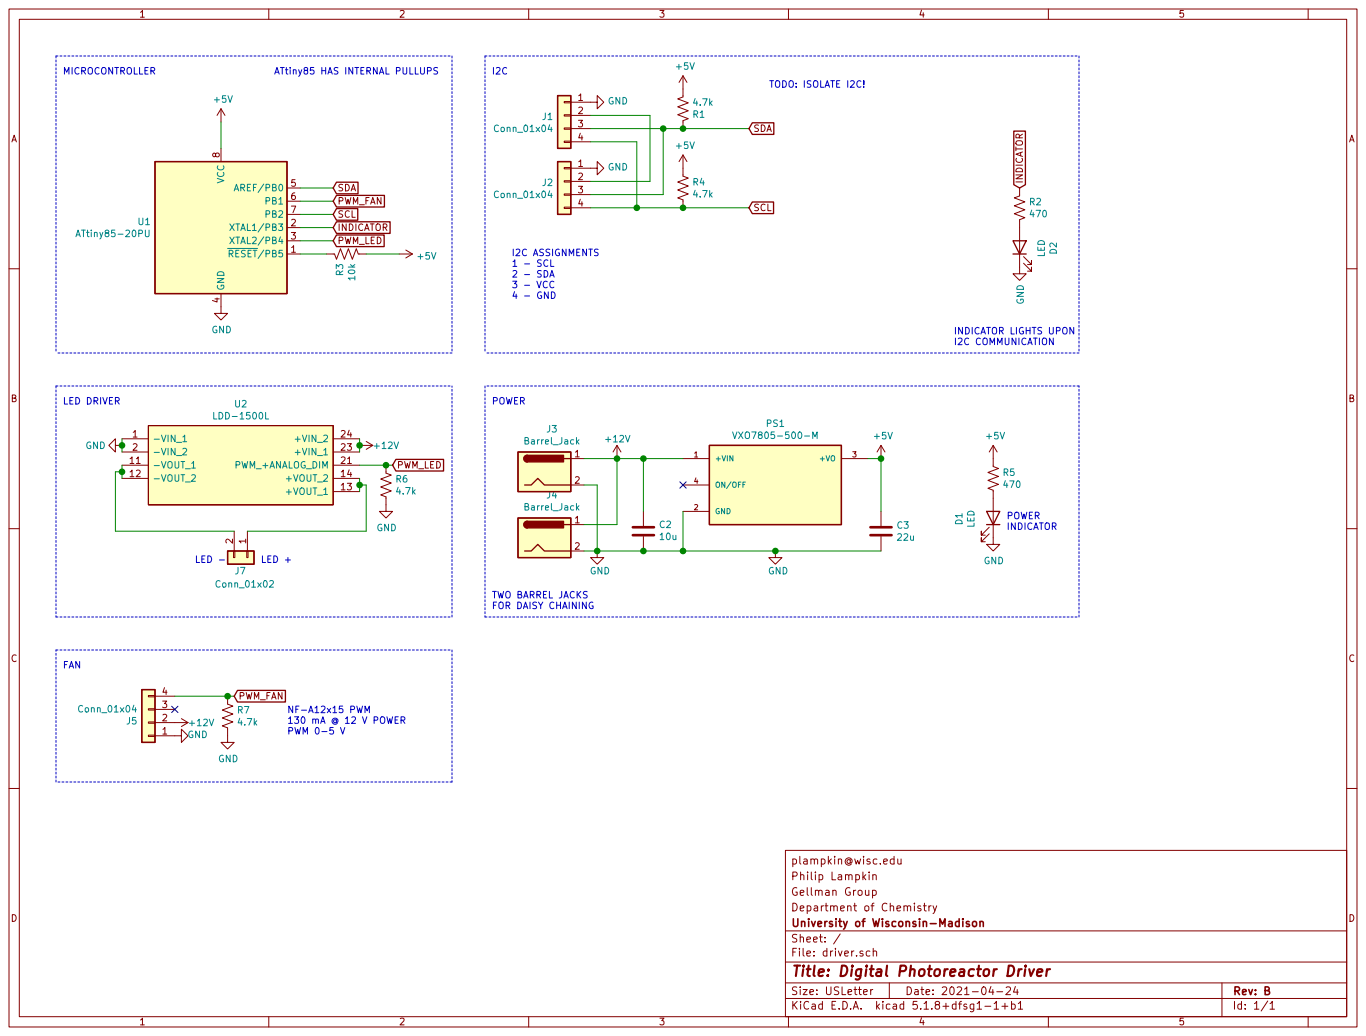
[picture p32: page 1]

TODO: ISOLATE I2C! TWO BARREL JACKS

SCL SDA NF-A12x15 PWM

Philip Lampkin
Gellman Group
Department of Chemistry
Id: 1/1 Title: Digital Photoreactor Driver File: driver.sch Sheet: / University of Wisconsin-Madison

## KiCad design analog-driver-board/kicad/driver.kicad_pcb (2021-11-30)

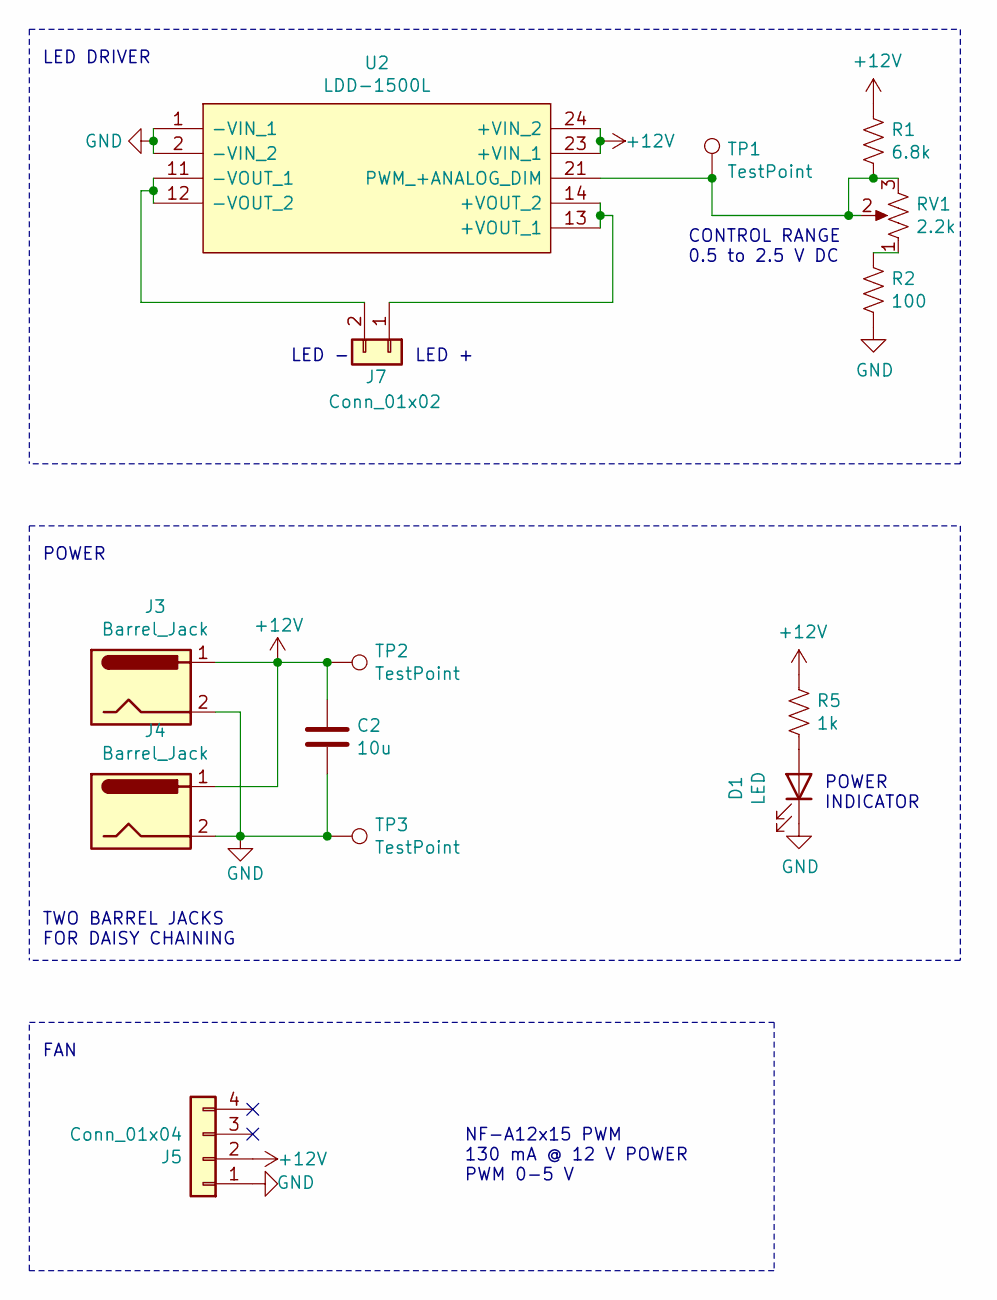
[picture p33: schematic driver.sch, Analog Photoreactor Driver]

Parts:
C2: 10u; C_1206_3216Metric_Pad1.33x1.80mm_HandSolder
D1: LED; LED_1206_3216Metric
J3, J4: Barrel_Jack; BarrelJack_Horizontal
J5: Conn_01x04; PinHeader_1x04_P2.54mm_Vertical
J7: Conn_01x02; PinSocket_1x02_P2.54mm_Vertical
R1: 6.8k; R_1206_3216Metric_Pad1.30x1.75mm_HandSolder
R2: 100; R_1206_3216Metric_Pad1.30x1.75mm_HandSolder
R5: 1k; R_1206_3216Metric_Pad1.30x1.75mm_HandSolder
RV1: 2.2k; TRIM_3362P-1-202TLF
TP1, TP2, TP3: TestPoint; TestPoint_THTPad_D3.0mm_Drill1.5mm
U2: LDD-1500L; LDD1500L; Manufacturer_Part_Number LDD-1500L; Mouser Part Number 709-LDD-1500L

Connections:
+12V: C2.2, J3.1, J4.1, J5.2, R1.1, R5.1, TP2.1, U2.23 (+VIN_1), U2.24 (+VIN_2)
GND: C2.1, D1.1 (K), J3.2, J4.2, J5.1, R2.2, TP3.1, U2.1 (-VIN_1), U2.2 (-VIN_2)
unnamed: D1.2 (A), R5.2
unnamed: J7.1, U2.13 (+VOUT_1), U2.14 (+VOUT_2)
unnamed: J7.2, U2.11 (-VOUT_1), U2.12 (-VOUT_2)
unnamed: R1.2, RV1.2, RV1.3, TP1.1, U2.21 (PWM_+ANALOG_DIM)
unnamed: R2.1, RV1.1

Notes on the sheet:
LED -
LED +
LED DRIVER
NF-A12x15 PWM 130 mA @ 12 V POWER PWM 0-5 V
FAN
TWO BARREL JACKS FOR DAISY CHAINING
POWER
POWER INDICATOR
CONTROL RANGE 0.5 to 2.5 V DC

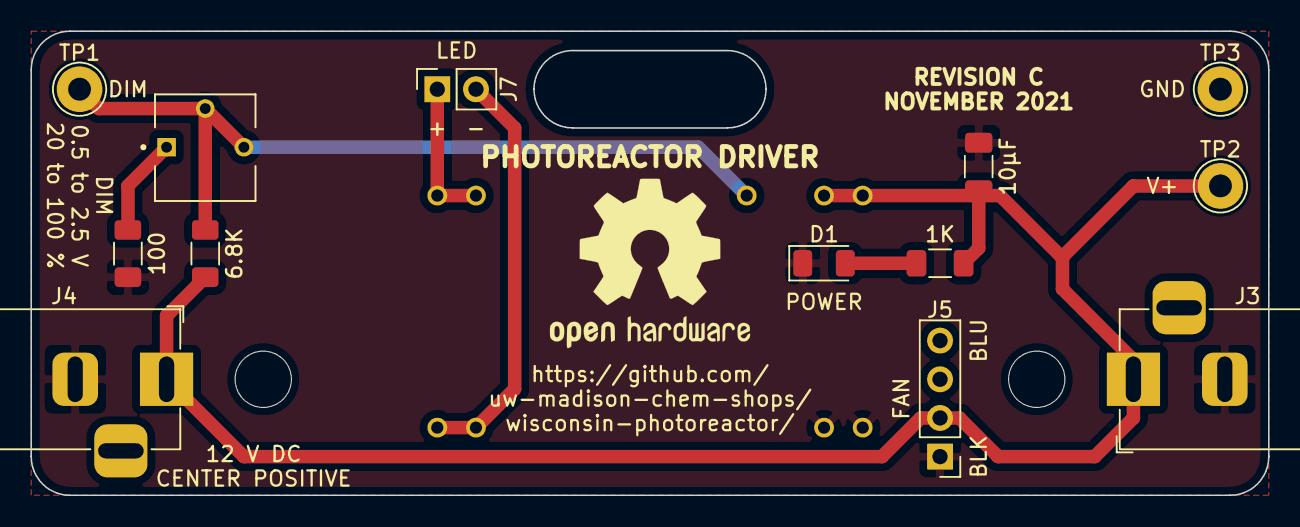
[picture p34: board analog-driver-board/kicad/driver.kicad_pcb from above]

Board: 2 copper layers, 81.3 x 30.5 mm, 14 parts (1 on the bottom side), 7 nets.

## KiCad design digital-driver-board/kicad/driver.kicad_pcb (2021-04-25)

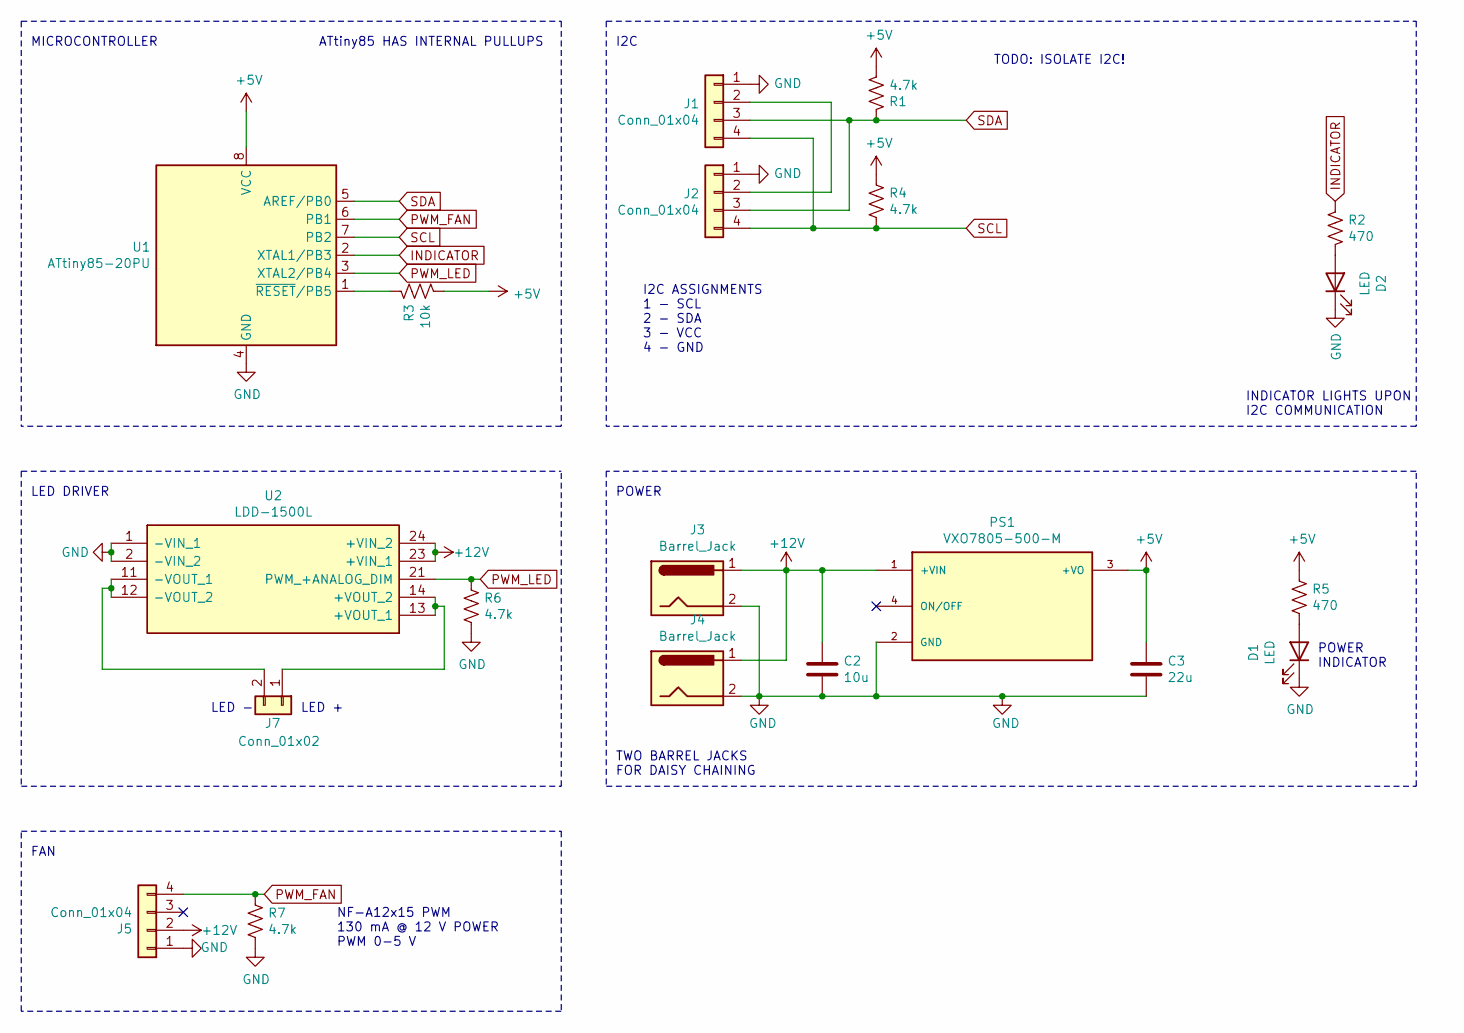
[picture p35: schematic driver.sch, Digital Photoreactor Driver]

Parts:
C2: 10u; C_1206_3216Metric_Pad1.33x1.80mm_HandSolder
C3: 22u; C_1206_3216Metric_Pad1.33x1.80mm_HandSolder
D1, D2: LED; LED_1206_3216Metric
J1, J2: Conn_01x04; JST_PH_S4B-PH-K_1x04_P2.00mm_Horizontal
J3, J4: Barrel_Jack; BarrelJack_Horizontal
J5: Conn_01x04; PinHeader_1x04_P2.54mm_Vertical
J7: Conn_01x02; PinSocket_1x02_P2.54mm_Vertical
PS1: VXO7805-500-M; CONV_VXO7805-500-M
R1, R4, R6, R7: 4.7k; R_1206_3216Metric_Pad1.30x1.75mm_HandSolder
R2, R5: 470; R_1206_3216Metric_Pad1.30x1.75mm_HandSolder
R3: 10k; R_1206_3216Metric_Pad1.30x1.75mm_HandSolder
U1: ATtiny85-20PU; DIP-8_W7.62mm_Socket
U2: LDD-1500L; LDD1500L; Manufacturer_Part_Number LDD-1500L; Mouser Part Number 709-LDD-1500L

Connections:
+5V: C3.1, PS1.3 (+VO), R1.2, R3.1, R4.1, R5.1, U1.8 (VCC)
+12V: C2.2, J3.1, J4.1, J5.2, PS1.1 (+VIN), U2.23 (+VIN_1), U2.24 (+VIN_2)
GND: C2.1, C3.2, D1.1 (K), D2.1 (K), J1.1, J2.1, J3.2, J4.2, J5.1, PS1.2 (GND), R6.2, R7.2, U1.4 (GND), U2.1 (-VIN_1), U2.2 (-VIN_2)
INDICATOR: R2.1, U1.2 (XTAL1/PB3)
unnamed: D1.2 (A), R5.2
unnamed: D2.2 (A), R2.2
unnamed: J1.2, J2.2
unnamed: J7.1, U2.13 (+VOUT_1), U2.14 (+VOUT_2)
unnamed: J7.2, U2.11 (-VOUT_1), U2.12 (-VOUT_2)
unnamed: R3.2, U1.1 (~RESET~/PB5)
PWM_FAN: J5.4, R7.1, U1.6 (PB1)
PWM_LED: R6.1, U1.3 (XTAL2/PB4), U2.21 (PWM_+ANALOG_DIM)
SCL: J1.4, J2.4, R4.2, U1.7 (PB2)
SDA: J1.3, J2.3, R1.1, U1.5 (AREF/PB0)

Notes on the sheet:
POWER
TWO BARREL JACKS FOR DAISY CHAINING
MICROCONTROLLER
ATtiny85 HAS INTERNAL PULLUPS
I2C ASSIGNMENTS 1 - SCL 2 - SDA 3 - VCC 4 - GND
POWER INDICATOR
LED -
LED +
LED DRIVER
FAN
INDICATOR LIGHTS UPON I2C COMMUNICATION
I2C
NF-A12x15 PWM 130 mA @ 12 V POWER PWM 0-5 V
TODO: ISOLATE I2C!

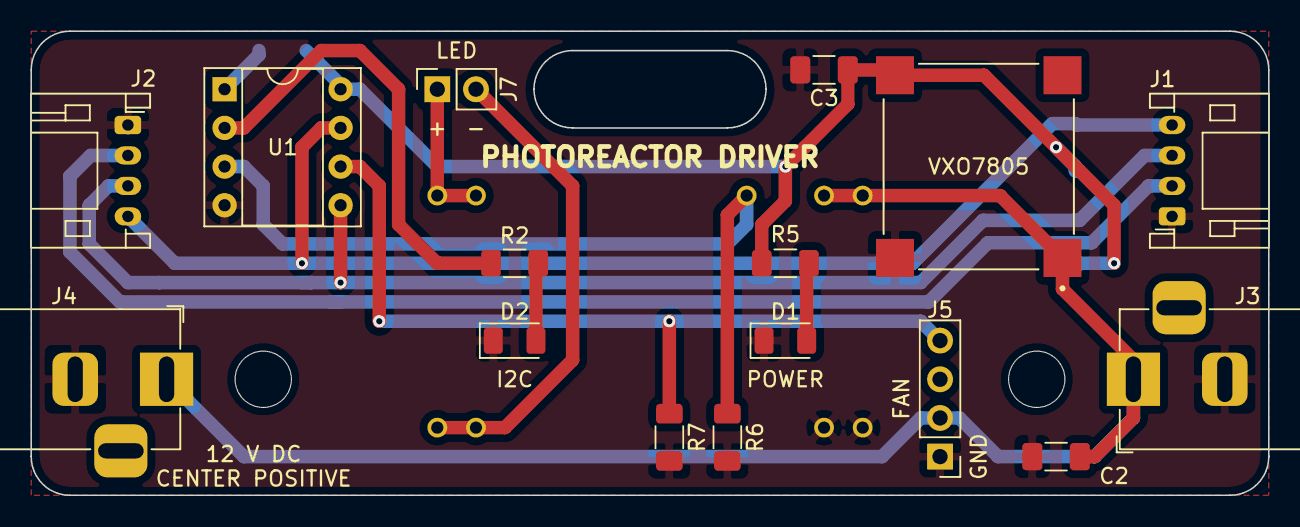
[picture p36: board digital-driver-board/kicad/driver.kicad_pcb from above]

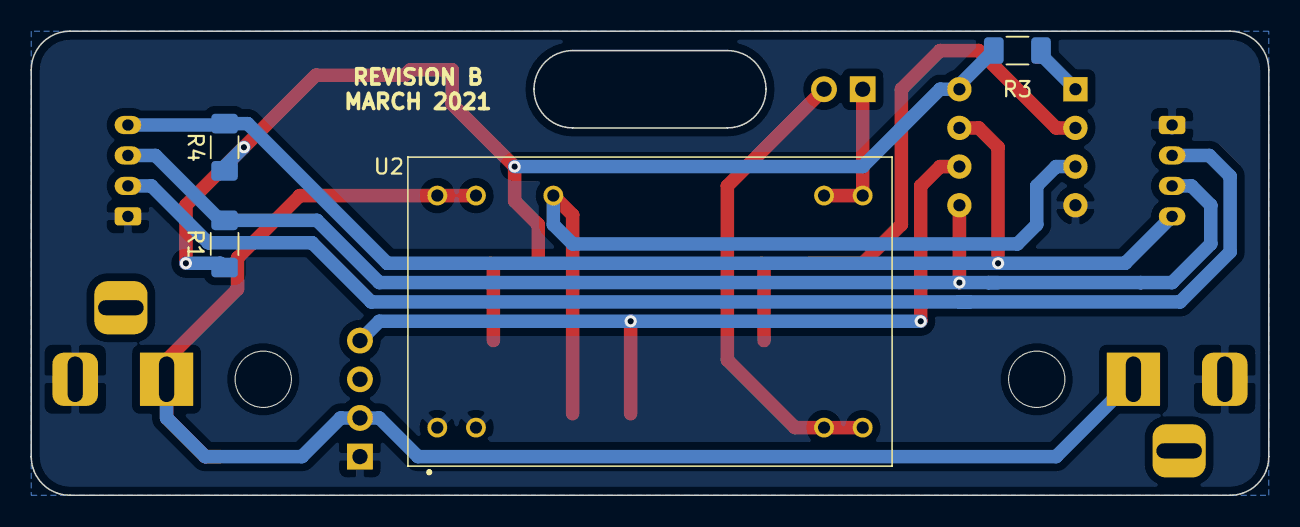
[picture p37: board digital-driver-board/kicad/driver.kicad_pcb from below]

Board: 2 copper layers, 81.3 x 30.5 mm, 20 parts (4 on the bottom side), 14 nets.

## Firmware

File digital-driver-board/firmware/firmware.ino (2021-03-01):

////////////////////////////////////////////////////////////////////////////////////
//       Digital Photoreactor Controller Slave Program Controlled by I2C          //
//                    Run this slave program on the AtTiny85.                     //      
////////////////////////////////////////////////////////////////////////////////////

#include "TinyWireS.h"                  // wrapper class for I2C slave routines   https://github.com/rambo/TinyWire/tree/master

#define I2C_SLAVE_ADDR  0x26            // I2C slave address (38, 0x26), 

uint8_t master_data[1];               // global buffer to store data sent from the master.
uint8_t master_bytes;                  // global variable to number of bytes sent from the master.

const int LEDPin = 4;                  //Arduino pin 4, pin 3 on AtTiny85 pinout
const int FanPin = 1;                  //Arduino pin 1, pin 6 on AtTiny85 pinout
const int BlinkPin = 3;                //Arduino pin 3, pin 2 on AtTiny85 pinout

void setup()
{
  // initialize the TinyWireS and usiTwiSlave libraries
  TinyWireS.begin(I2C_SLAVE_ADDR);      // init I2C Slave mode

  // register the onReceive() callback function
  TinyWireS.onReceive(receiveEvent);
  
  pinMode(LEDPin, OUTPUT);   // set pin for LED PWM
  pinMode(FanPin, OUTPUT);   // set pin for Fan PWM
  pinMode(BlinkPin, OUTPUT); // set pin to blink LED
  
  TCCR0B = TCCR0B & 0b11111000 | 0b001; // sets internal timer of AtTiny85 to 31250 Hz for fast PWM for controlling fan speed
}

// Gets called when the ATtiny85 receives an I2C write slave request
void receiveEvent(uint8_t num_bytes)
{
  uint8_t i;
  
  // save the number of bytes sent from the master
  master_bytes = num_bytes;

  // store the data from the master into the data buffer
  for (i = 0; i < master_bytes; i++)
    master_data[i] = TinyWireS.receive();

  // set LED and Fan PWM duty to random byte values recieved from the master
  analogWrite(FanPin, master_data[0]);
  analogWrite(LEDPin, master_data[1]);

  // blink LED whenever data is successfuly recieved
  digitalWrite(BlinkPin, HIGH);
  delay(10);
  digitalWrite(BlinkPin, LOW);

}

void loop()
{
  
}

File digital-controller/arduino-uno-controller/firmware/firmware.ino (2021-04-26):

/* EXAMPLE FIRMWARE
 * CONTROLLING WPP DRIVERS FROM ARDUINO UNO
 * 
 * SERIAL INTERFACE
 * 9600 baud
 * newline terminated (no carriage return)
 * space separated commands:
 * <ADDRESS> <LED INTENSITY> <FAN INTENSITY>
 * 
 * example: full brightness full speed:
 * 38 255 255
 * example: LED off fan full speed:
 * 38 0 255
 * example: LED medium fan off
 * 38 100 0
 * 
 * if <ADDRESS> 0, commands sent to all devices
 * 
 * if <ADDRESS> -1, list of addresses seen returned
 */

#include <Wire.h>

#define INPUT_SIZE 100  // TODO: make this a reasonable value
#define sep " "
char input[INPUT_SIZE + 1];

char c_address = '0';
char c_led = '0';
char c_fan = '0';
int address = 0;
int led = 0;
int fan = 0;

void setup() {
  pinMode(A4, OUTPUT);
  pinMode(A5, OUTPUT);
  Wire.begin(); 
  Serial.begin(9600);
}

void loop() {
}

void scan() {
  Serial.println("scanning!");
  byte error, address;

  for(address = 1; address < 127; address++ ) 
  {
    // The i2c_scanner uses the return value of
    // the Write.endTransmisstion to see if
    // a device did acknowledge to the address.
    Wire.beginTransmission(address);
    error = Wire.endTransmission();

    if (error == 0)
    {
      Serial.print("I2C device found at address ");
      Serial.println(address);
    } 
  }
  
}

void serialEvent() {  // occurs whenever new data comes in the hardware serial RX
  // read serial into input char array
  byte size = Serial.readBytesUntil('\n', input, INPUT_SIZE);
  input[size] = 0;
  // parse input
  char *c_address = strtok(input, sep);
  char *c_led = strtok(0, sep);
  char *c_fan = strtok(0, sep);
  // convert input
  address = atoi(c_address);
  led = atoi(c_led);
  fan = atoi(c_fan);
  // scan if address is less than zero
  if (address < 0) {
    scan();
  }
  // write to peripheral
  uint8_t buf[1];
  buf[0] = fan;
  buf[1] = led;
  Wire.beginTransmission(address);
  Wire.write(buf, 2);
  Wire.endTransmission();
}

void serialEventRun(void) {
  // this runs inside of the main loop, essentially
  if (Serial.available()) serialEvent();
}

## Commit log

2020-12-29 updated PCB w/ LED
    [Digital Photoreactor Controller.kicad_pcb]
2020-12-30 Commented and added blink LED function on receive data
2020-12-30 Updated PCB routing
    [Digital Photoreactor Controller.kicad_pcb]
2020-12-30 Updated drill marks and edgecuts to be more uniform
    [Digital Photoreactor Controller.kicad_pcb]
2020-12-30 Added optimized lightsource bases in open and closed configuration
    [lightsource_base_closed v1.skp, lightsource_base_closed v1.stl, lightsource_base_open v1.skp, lightsource_base_open v1.stl]
2021-01-06 Removed version numbers, removed open base, added final optimized closed base design
    [lightsource_base_closed v1.skp, lightsource_base_closed v1.stl, lightsource_base_open v1.skp, lightsource_base_open v1.stl]
2021-01-19 restructure repository
    [AL8805W5-7.step, Analog PR Controller-job.gbrjob, Analog PR Controller.kicad_pcb, Analog PR Controller.sch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]
2021-01-19 cleanup analog photoreactor
    [driver.kicad_pcb, driver.sch]
2021-01-19 cleanup digital driver
    [Digital Photoreactor Controller.sch, driver.kicad_pcb, driver.sch]
2021-01-21 updated base to use heat insets, have compatability with zip tie anchors and better mounts for driver board
    [lightsource_base_closed.stl]
2021-01-25 digital driver prototype
    [driver-B_Cu.gbr, driver-B_Mask.gbr, driver-B_Paste.gbr, driver-B_SilkS.gbr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]
2021-01-25 digital-driver readme
    [driver-B_Cu.gbr, driver-B_Mask.gbr, driver-B_Paste.gbr, driver-B_SilkS.gbr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]
2021-01-27 digital driver 1.0.0
    [driver.sch, driver.sync-conflict-20210125-095746-UKY5OD3.sch, driver.sync-conflict-20210125-095808-UKY5OD3.kicad_pcb]
2021-01-29 analog driver 1.0.0
    [AL8805W5-7.step, Analog PR Controller-job.gbrjob, LDD-1500L.stl, LDD-1500L.stp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]
2021-02-11 updated base designs
    [Digital Photoreactor Controller.sch, lightsource_base.stl, lightsource_base_closed.stl]
2021-03-05 analog-driver revision B
    [driver-B_Cu.gbr, driver-B_Mask.gbr, driver-B_Paste.gbr, driver-B_SilkS.gbr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]
2021-03-05 rearrange repository
    [1dram_mirrorbox v1.f3d, 1dram_mirrorbox v1.skp, 1dram_mirrorbox v1.stl, 1dram_top v1.f3d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]
2021-03-06 added enclosures for new vessel types, added WPR logo to base and cleaned up file names
    [1dram_mirrorbox v1.f3d, 1dram_mirrorbox v1.skp, 1dram_mirrorbox v1.stl, 10mLSchlenk_chamber.f3d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]
2021-03-06 added LED emission spectra
    [led-emission-spectra.xlsx]
2021-03-06 digital driver revision B
    [driver-B_Cu.gbr, driver-B_Mask.gbr, driver-B_Paste.gbr, driver-B_SilkS.gbr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]
2021-03-12 updated amber spectrum
    [led-emission-spectra.xlsx]
2021-03-25 organize analog-driver
    [driver.kicad_pcb, driver.sch]
2021-03-25 assembly instructions skeleton
2021-04-14 assembly skeleton
2021-04-16 pcb assembly pictures
2021-04-16 led pictures
2021-04-19 first minimum viable assembly instructions
2021-04-24 added typical photon source emission spectra
    [led-emission-spectra.xlsx]
2021-04-24 reworked LED emission spectra terminology
2021-04-24 updated LED terminology
2021-04-24 rename leds directory
    [led-emission-spectra.xlsx]
2021-04-24 terminology update
    [10mLSchlenk_chamber.f3d, 10mLSchlenk_chamber.stl, 10mLSchlenk_top.stl, 1dram_chamber.f3d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]
2021-04-24 terminology updates
    [10mLSchlenk_chamber.f3d, 10mLSchlenk_chamber.stl, 10mLSchlenk_top.stl, 1dram_chamber.f3d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]
2021-04-24 remove wisconsin crest logo
    [driver-B_Cu.gbr, driver-B_Mask.gbr, driver-B_Paste.gbr, driver-B_SilkS.gbr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]
2021-04-27 cleaned up digital driver board portion
2021-04-27 document fan, led connectors
2021-04-27 added completed digital board figure
2021-05-18 Fixed photoreactor base naming, WPP branding and heat inset depth
    [lightsource_base.stl, photoreactor_base.stl]
2021-05-18 updated 1mL to 2mL and item number
    [2mL-03-338AA-chamber.f3d, 2mL-03-338AA-chamber.stl, 2mL-03-338AA-holder.f3d, 2mL-03-338AA-holder.stl]
2021-05-18 updated fab guide 1mL to 2mL
2021-05-18 Update README.md
    added links to LED stars from LEDsupply
2021-05-24 added light shield
    [light_shield.f3d, light_shield.stl]
2021-05-26 Updated test point voltage --> LED intensity
2021-11-30 add url to analog driver board
    [driver-B_Cu.gbr, driver-B_Mask.gbr, driver-B_Paste.gbr, driver-B_SilkS.gbr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]
